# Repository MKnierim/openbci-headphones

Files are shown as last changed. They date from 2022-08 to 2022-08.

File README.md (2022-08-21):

# OpenBCI Headphones
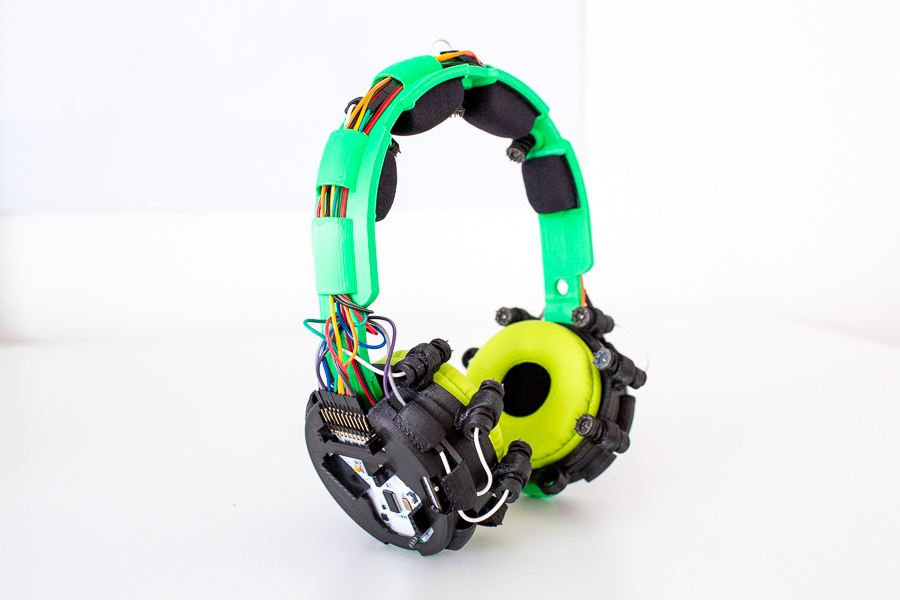
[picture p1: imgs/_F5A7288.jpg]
"The OpenBCI Headphones" The OpenBCI Headphones


If we want our science and technology to grow faster, we need to get more people on it, right?

This repository contains the description and materials for turning the OpenBCI EXG biosignal acquisition system into 
a pair of functional headphones that can also record EEG, EMG, and ECG.

A first validation study is accepted for publication at the <a href="research/Knierim et al. (forthcoming).pdf">43rd International Conference on Information Systems, Copenhagen 2022</a>. You can find the authors' version of this study in the <a href="research/">research</a> folder.

Please take a look at the sections below and the other repository files for assembly details.

If you have any questions, feedback or suggestions, please feel free to send a message to contact@expeeeriments.io

------

# Resources
This project could not have been completed without the wonderful work by other open-source projects. 
Basically, this work is based heavily on these three projects:

1. <a href="https://docs.openbci.com/" target="_blank">OpenBCI</a> (Biosensing Components)
2. <a href="http://www.print.plus/" target="_blank">Print.Plus Headphones</a> (Headphones Design)
3. <a href="https://homebrewheadphones.com/" target="_blank">HomeBrew Headphones</a> (Audio Speakers)

All materials of those (and this project) are available under the Creative Commons Share-alike 4.0 International license.

------

# List of Materials

| Amount | Part   Description                                                  | Instance /   Reference                                                                                               |
|--------|---------------------------------------------------------------------|----------------------------------------------------------------------------------------------------------------------|
| 1      | OpenBCI Cyton Board + Ultracortex Electrodes   (Biosignal Acquisition Kit) | Available from the manufacturer at: https://shop.openbci.com/products/d-i-y-neurotechnologists-starter-kit?variant=13043169493064   |
| 1      | 3D-Printed Headphones Kit (incl. Headband, Speakers, and Electrodes)  | Custom [3D-Print Files](./stl/) available in this repository                                                        |
| 1      | Headband Cushion (kwmobile Sennheiser HD545 replacement)             | Available, e.g. at: https://www.amazon.de/gp/product/B08C57V9H9/ref=ppx_yo_dt_b_asin_title_o00_s00?ie=UTF8&psc=1             |
| 2      | Ear Cushions (70mm diameter)                                         | Available, e.g. at: https://de.aliexpress.com/item/1005002212424250.html?gatewayAdapt=glo2deu&spm=a2g0o.9042311.0.0.dcd44c4deRtu6F             |
| 2      | Audio Drivers (Dayton Audio CE38MB-32 1-1/2"" Mini Speaker)          | Available, e.g. at: https://www.parts-express.com/Dayton-Audio-CE38MB-32-1-1-2-Mini-Speaker-Black-32-Ohm-285-131                               |
| 2      | Audio Jacks (2.5mm)                                                  | Available, e.g. at: https://www.amazon.de/gp/product/B009D5388O/ref=ox_sc_act_title_1?smid=A2X1ST6CC1USDW&psc=1                               |
| 2      | Hookup Wire (4x10cm long)                                            | Available, e.g. at: https://www.adafruit.com/product/288                               |
| 1      | Speaker Cable (Sol Republic Master Tracks HD V8 V10 V12 X3)          | Available, e.g. at: http://shorturl.at/szBKM                               |
| 10     | Jumper Connector Cables Female-Male (10cm, 20cm & 40cm)              | Available, e.g. at: https://www.adafruit.com/product/1953                                                      |
| 1      | Lithium Ion Polymer Battery - 3.7v 500mAh (JST-PH Connector)             | Available, e.g. at: https://www.adafruit.com/product/1578
| 1      | Lithium Ion Polymer Battery 500mm Extension Cable (JST-PH Connector)        | Available, e.g. at: https://www.adafruit.com/product/1131                                          

Lastly, in terms of **tools**, you will definitely need: 

- Soldering iron (to assemble the audio drivers)
- Small screwdriver (to assemble the electrodes)
- Pair of scissors (to cut the headband cushion)

------

# Assembly Instructions
To put the headphones together, you need to first make sure that you have all the required components ready. 
That means sourcing the components and, if you decide so, 3D-printing the headphone parts.
The picture below shows all components and required tools in one place.

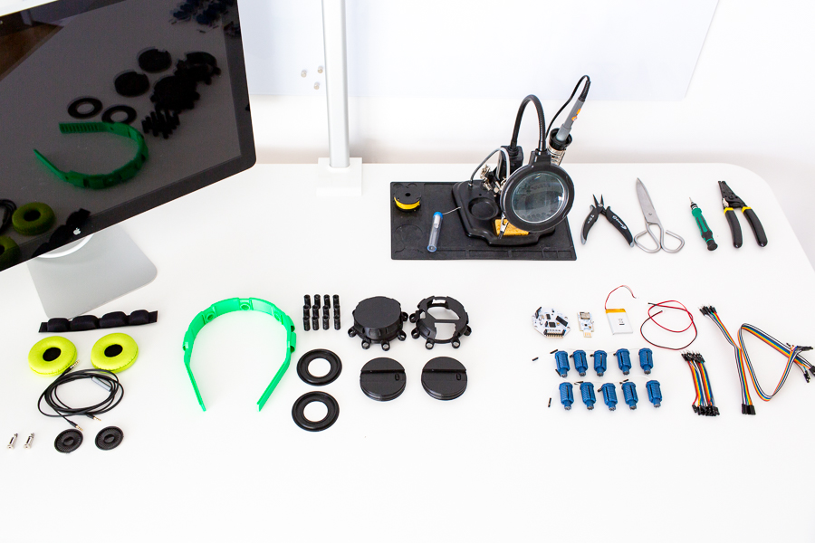
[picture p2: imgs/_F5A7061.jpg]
"All Components Laid Out" All Components Laid Out

 
## 3D-Print the Parts
All of the 3D-printed parts can be manufactured using a regular desktop FDM printer with a 0.4mm brass nozzle and consumer-grade plastics (e.g. PLA).
Importantly, you don't have to set up any particular support structures. These are either not required or already modeled in.
However, some of the parts have particular requirements in terms of stiffness and strength. Therefore, we recommend selecting
appropriate materials for these parts. 

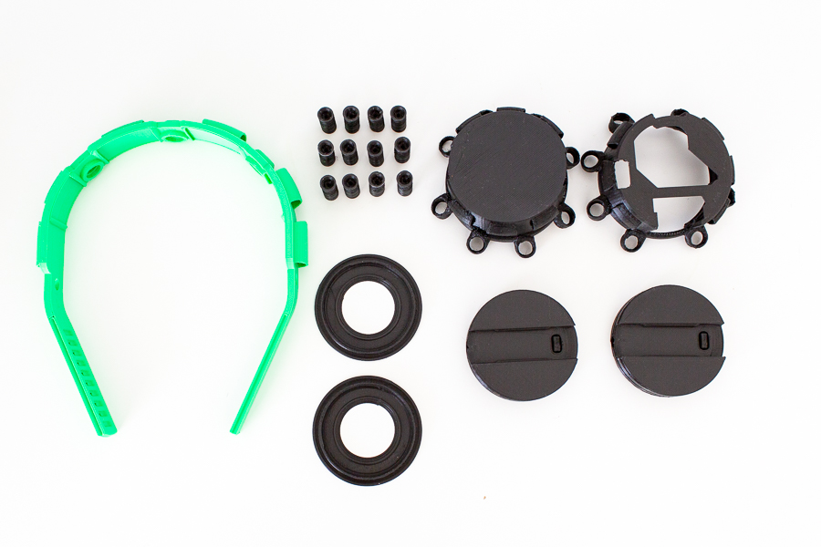
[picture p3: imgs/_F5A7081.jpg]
"All 3D-Printed Parts Laid Out" All 3D-Printed Parts Laid Out
 

### Headband
It is of particular importance for the headband to achieve a high level of flexibility (a low level of stiffness).  
As the headband must bend sufficiently, a more elastic material prevents the headband from breaking during regular use.
Believe us, it happened more times than we'd like to admit during testing... Nevertheless, that helped us figure out suitable materials.
To date, we used the <a href="https://www.extrudr.com/en/products/catalogue/pla-nx2-signalgrun_1980/" target="_blank">PLA NX2 from extrudr</a> 
as it provides the highest material flexibility that we found. The <a href="https://www.ultrafusefff.com/product/ultrafuse-pla-blue-1-75mm-750g/" target="_blank">Ultrafuse PLA from BASF</a>
also works fairly well, as does the <a href="https://fiberlogy.com/en/fiberlogy-filaments/filament-easy-pla/" target="_blank">EASY PLA from fiberlogy</a>. In contrast, the <a href="https://www.extrudr.com/en/products/catalogue/green-tec-pro-schwarz_2284/" target="_blank">GreenTEC Pro from extrudr</a>, 
which we recommend for parts that need to be robust was found to be much too stiff for good use with the headband.

Beyond the right material, it is only important to prevent warping during the print, as already low warping levels can cause the 
electrode holes to become distorted and unusable. Therefore, we recommend printing at lower temperatures and slow speeds to allow for sufficient material cooling. 
A layer height of 0.2mm is sufficient for this part. Also, you might want to try to print with low infill to retain the flexibility (5-10%).

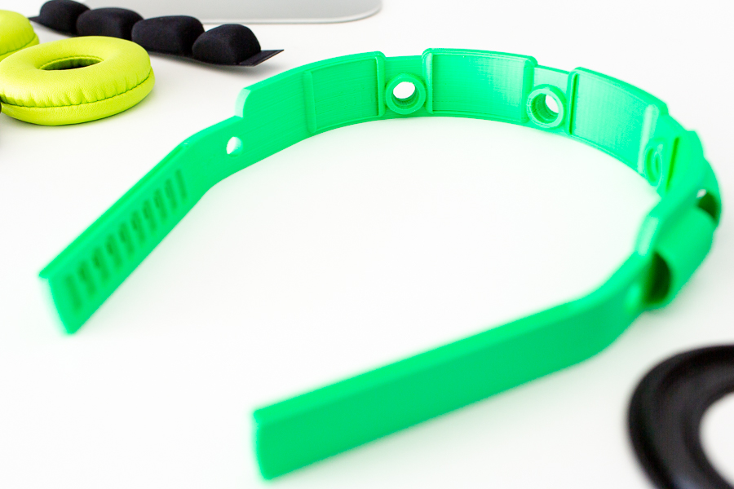
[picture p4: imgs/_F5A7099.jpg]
"The 3D-Printed Headband - PLA NX2" The 3D-Printed Headband - PLA NX2


### Electrodes
As mentioned above, we recommend using a material with high stiffness like the <a href="https://www.extrudr.com/en/products/catalogue/green-tec-pro-schwarz_2284/" target="_blank">GreenTEC Pro from extrudr</a> to print the spring electrodes. 
This material also provides the advantage that it basically does not warp at all. With good retraction settings and 
slow print speeds, you can achieve robust and clean spring electrode prints. 
Also, we printed our electrodes with 0.1mm layer height to make the overhangs print cleaner.

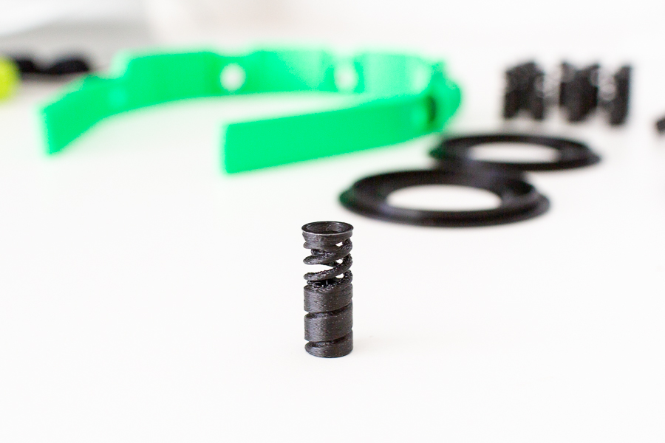
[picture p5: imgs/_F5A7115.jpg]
"The 3D-Printed Spring Electrodes - GreenTEC Pro" The 3D-Printed Spring Electrodes - GreenTEC Pro

 
### Remaining Parts
The remaining parts don't have any particular requirements for printing. You can choose a material that you prefer and 
print them with a regular layer height of 0.2mm at moderate speeds (30-40 mm/s). 
In our screenshots, we used the <a href="https://www.extrudr.com/en/products/catalogue/green-tec-pro-schwarz_2284/" target="_blank">GreenTEC Pro</a> material again for these parts.
 
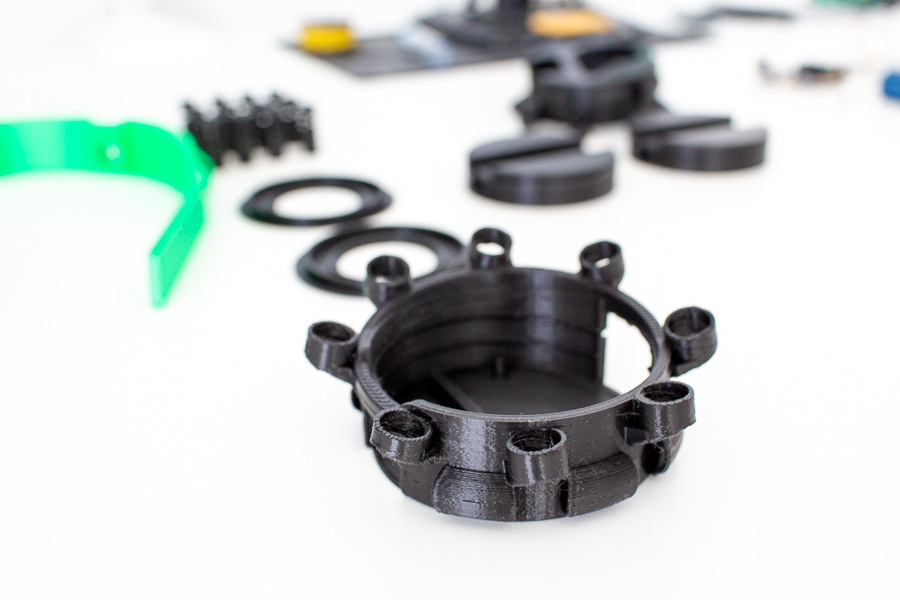
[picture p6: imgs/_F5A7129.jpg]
"The Remaining 3D-Printed Parts - GreenTEC Pro" The Remaining 3D-Printed Parts - GreenTEC Pro


## Electrode Assembly
To finalize the spring electrodes, you need to convert the OpenBCI Ultracortex MK IV electrodes next.
This step is pretty straightforward. 
Use a small screwdriver to screw off the spike electrodes from their original bodies.

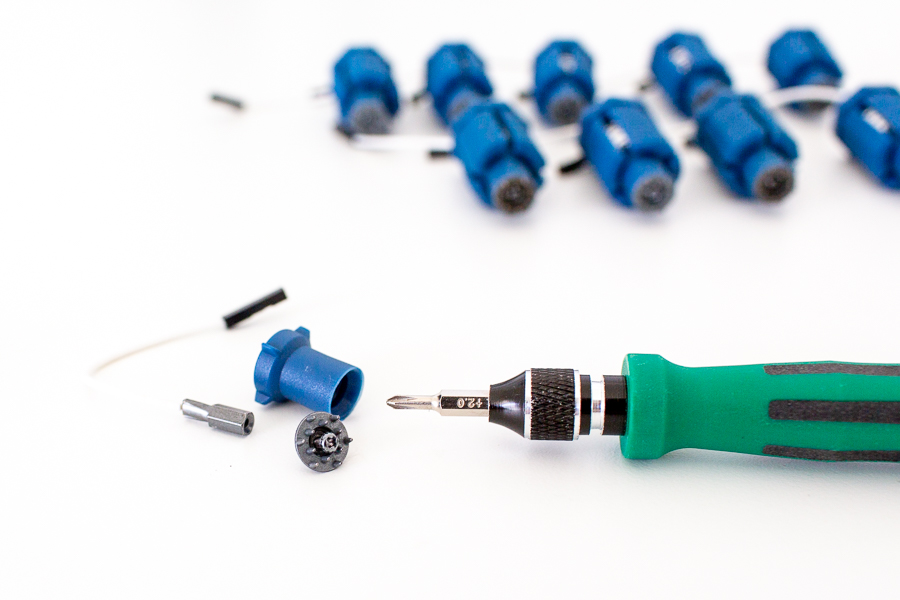
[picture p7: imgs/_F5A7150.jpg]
"Dismantling the OpenBCI Electrodes" Dismantling the OpenBCI Electrodes

 
Afterwards, place first the terminal into the spring electrode. You might have to use your screwdriver to push them in.
Be careful, though, to not damage the cable as it can fairly easily become separated if you apply too much force at the end of the crimp terminal.
Once the terminal is inserted, place the spike electrode on the top, push the electrode together slightly and tighten the screw again. 
Do this a couple of times, and voilà - you have a nice set of 3D-printed headphone electrodes. 

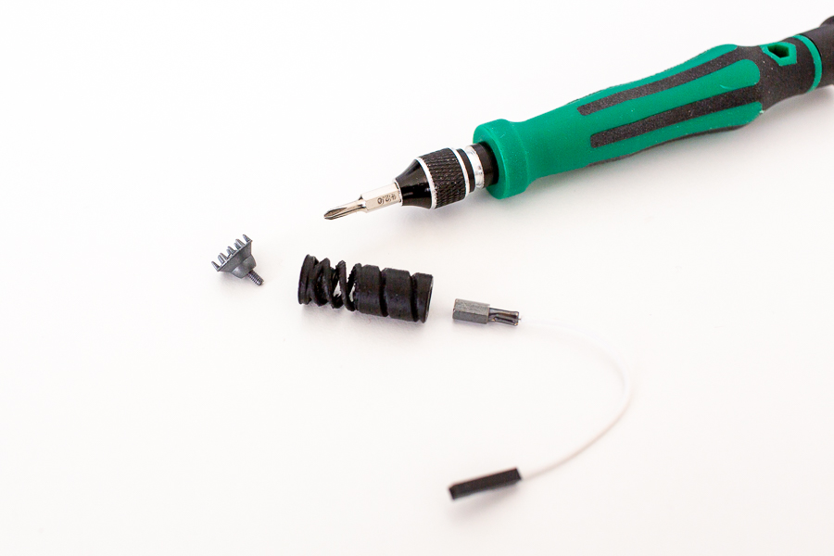
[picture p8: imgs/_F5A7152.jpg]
"Assemble the Spring Electrodes" Assembling the Spring Electrodes


## Cushion Assembly
Next, you can ready the headband and speaker covers by attaching the cushions. 
Having these cushions is super important to achieve decent wearing comfort.
To complete this step, you will require only a pair of scissors.

The headband cushion piece can be cut off at the bridges between the pads.

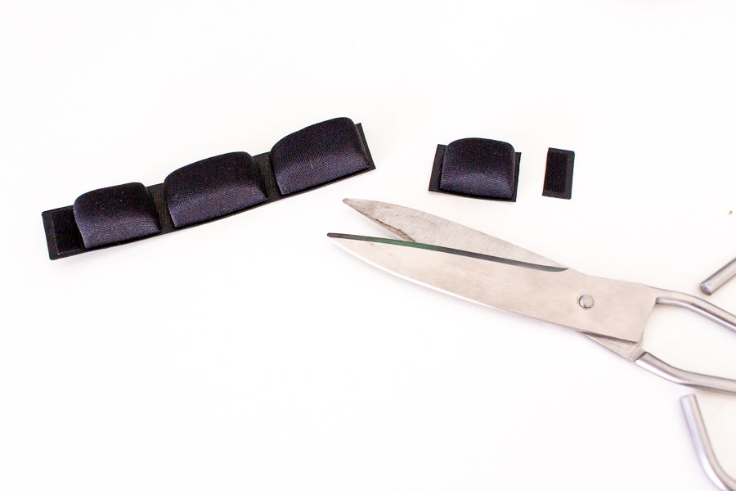
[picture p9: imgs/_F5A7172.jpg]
"Cutting the Headband Pad into Pieces" Cutting the Headband Pad into Pieces
 

Once you have done this, you can start inserting the individual pads into the headband. 
It might take a few tries to cut them to the correct size. 
Leave a slight overhang at each pad to make sure the pad is kept in place by some pressure. 

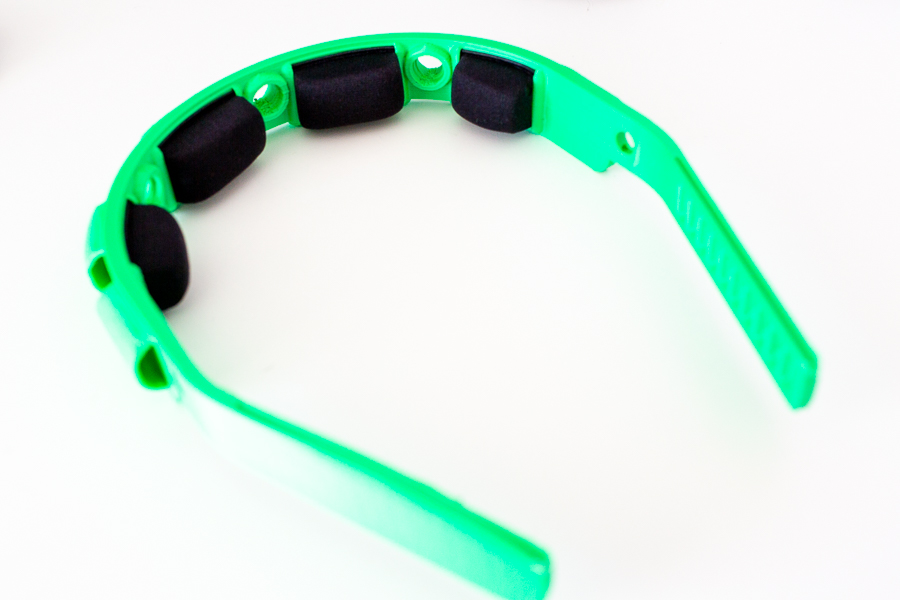
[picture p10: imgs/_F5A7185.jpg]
"Placing the Cushions into the Headband" Placing the Cushions into the Headband


For the speaker cover, stretch the fabric a bit over the cover to attach the cushion.
Piece of cake. It can take some fabric wrestling, though, on the first try.

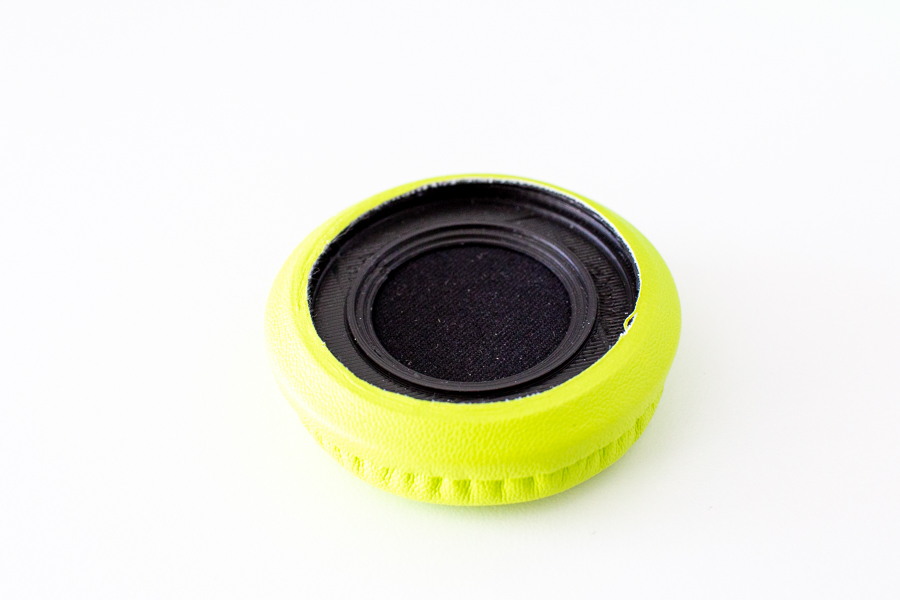
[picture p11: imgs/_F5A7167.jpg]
"Placing the Ear Cushions over the Speaker Cover" Placing the Ear Cushions over the Speaker Cover


## Speaker Assembly
For the assembly of the speaker, we folloed the instructions of the <a href="https://homebrewheadphones.com/build/" target="_blank">HomeBrew Headphones</a> closely. 
You could follow that link and get the same (and extended) instructions. We just include them here again for completeness.

First, you need to solder the hookup wire to the 2.5mm jacks. 
Cut the hookup wire into four approx 2″ or 5cm lengths and strip the insulation from about 1/8″ or 3mm from the ends.
If you are using the recommended jacks, solder the negative (green) wire onto the large tab and the positive (yellow) onto the small round one.

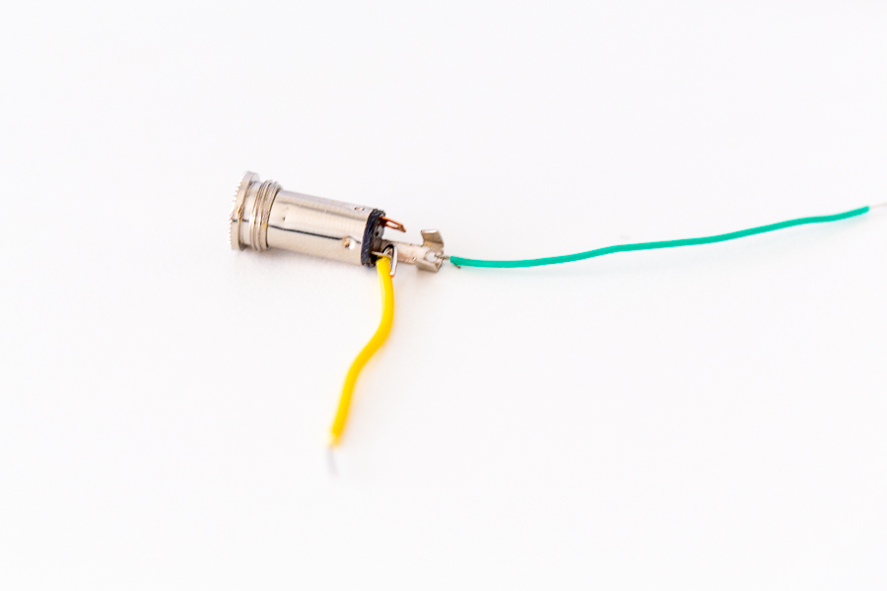
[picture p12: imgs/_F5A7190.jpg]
"Audio Jacks with Soldered Wires" Audio Jacks with Soldered Wires


Next, you can place the audio jacks and drivers into the speaker housing (see picture below).
Be careful not to damage the fragile mylar film in the drivers.
Afterwards, you can solder the hookup wires to the audio drivers. 
The red terminal is positive, and the other is negative. 
You won’t need any solder for this – melt the solder tab on the driver with your soldering iron, then insert the wire into the puddle and remove the iron while still holding the wire until the solder solidifies. 
Be careful not to apply too much heat, as this may damage the driver.

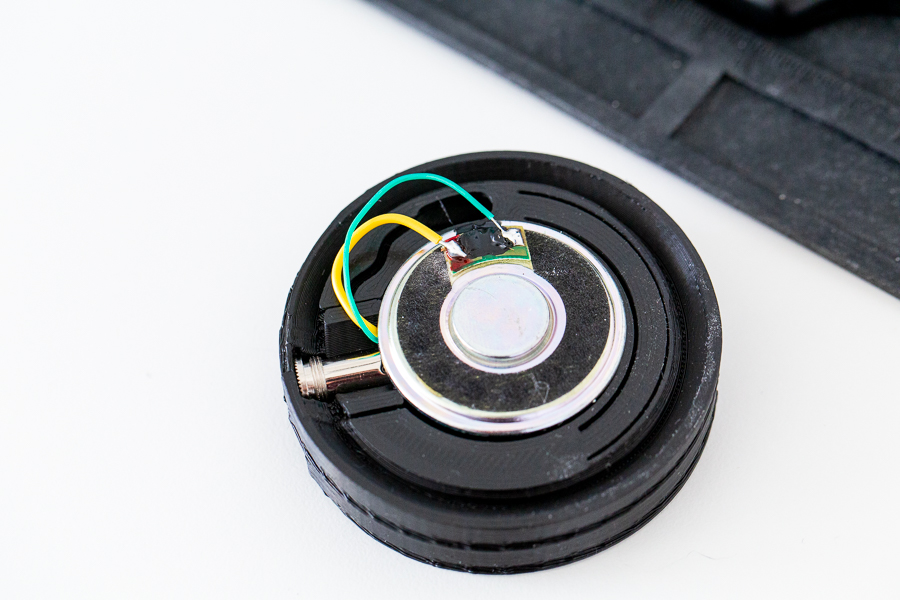
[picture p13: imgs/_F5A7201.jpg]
"Audio Driver Connected to Audio Jack" Audio Driver Connected to Audio Jack


If you would like to tune the sound, please take a look at the <a href="https://homebrewheadphones.com/build/" target="_blank">HomeBrew Headphones build instructions</a> where a thorough documentation is provided for this step.

Finally, to complete the speaker assembly, place the speaker cover with the ear cushions on top and twist to lock them in place. Ta daaaa - you have got some real headphone speakers - assembled all by yourself!

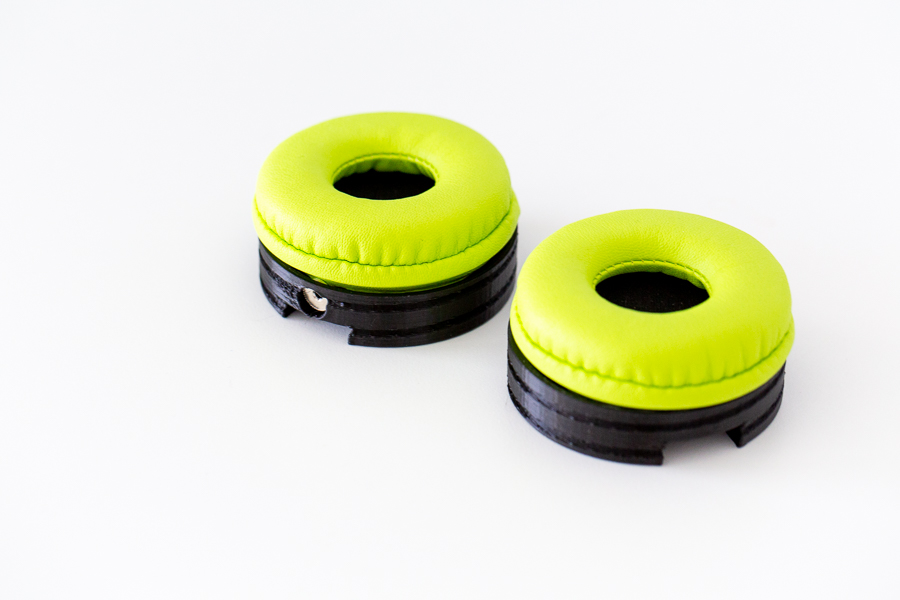
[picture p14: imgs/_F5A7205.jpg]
"Assembled Left and Right Speakers" Assembled Left and Right Speakers


## Electronics Assembly
After all components are ready, you can now finally put the headset together. 
To do this, first, place the battery and Cyton board into the electronics enclosures.
For the Cyton board, attach the battery extension cable already.

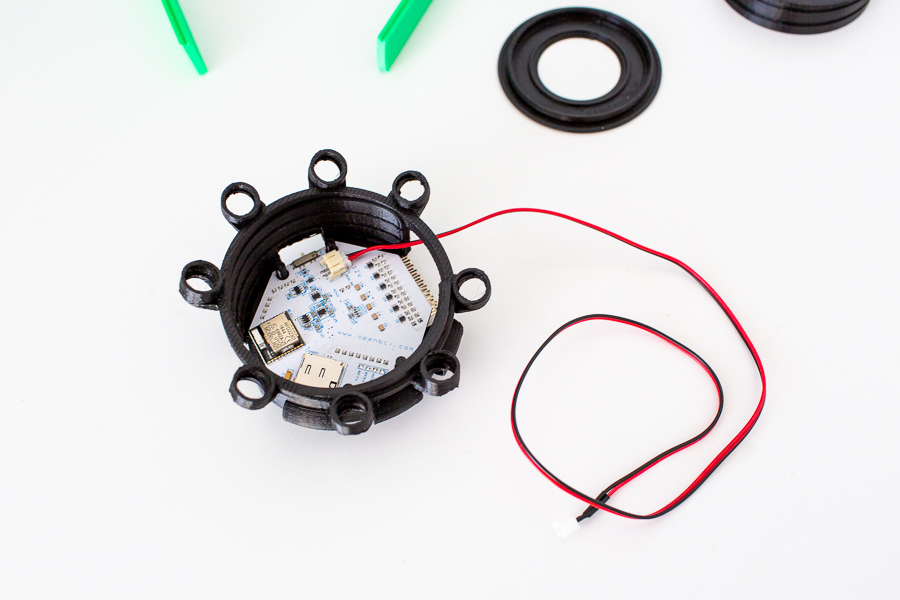
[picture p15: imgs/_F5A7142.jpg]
"Cyton Board in Housing" Cyton Board in Housing

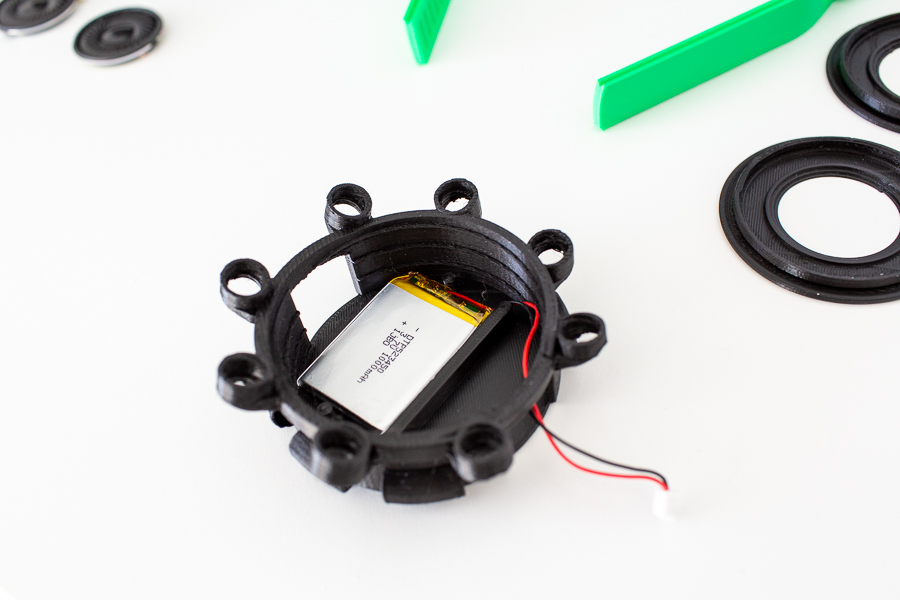
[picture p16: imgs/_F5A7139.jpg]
"LiPo Battery in Housing" LiPo Battery in Housing
 

Now, screw in the assembled speakers. Make sure that the battery cables are sticking out of the enclosure for this.

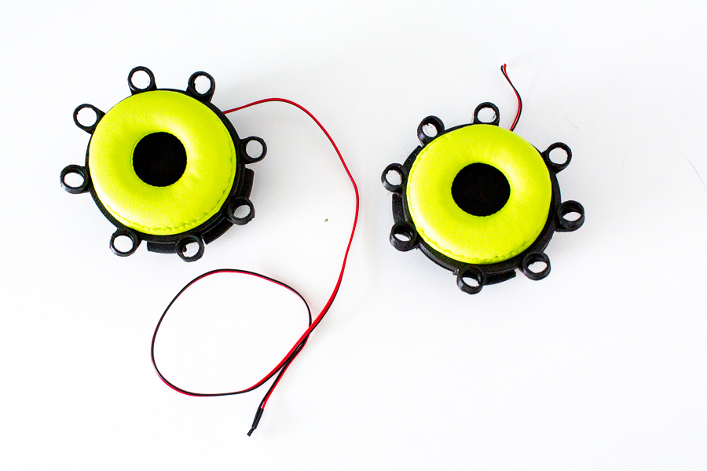
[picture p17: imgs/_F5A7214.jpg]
"Speakers and Electronics Housings Joined" Speakers and Electronics Housings Joined
 

Next, attach the headband to both the left and right speakers. After this, you can route the battery cable from 
the left to the right ear. Test if the Cyton board can be powered on before continuing.
  
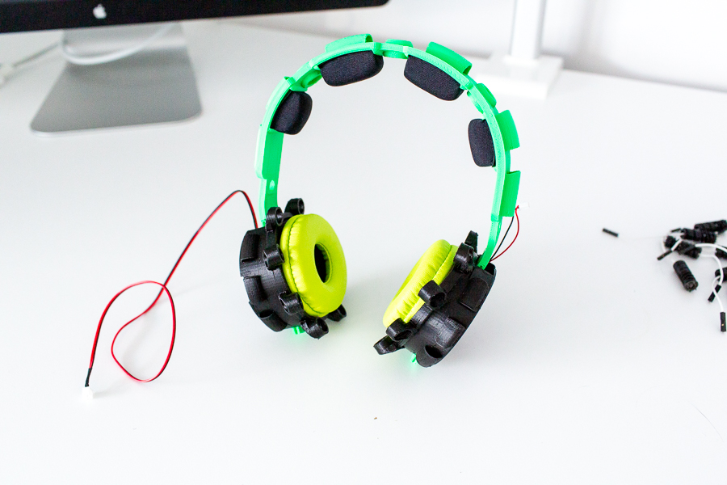
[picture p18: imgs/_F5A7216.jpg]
"Headband and Speakers Combined" Headband and Speakers Combined


At this stage, things are starting to look like headphones, right? Now the only thing left to do is to attach the
electrodes. No electrodes - no electrophysiological sensing. The electrodes screw in the holders easily. Before you start
screwing around, you should take a second though, to consider which electrode positions you would like to use in your recordings.
As the Cyton board can only fit 8 channels (+ reference and ground electrode), your selection for the electrode positions
should be rooted in the phenomenon you are interested in measuring.

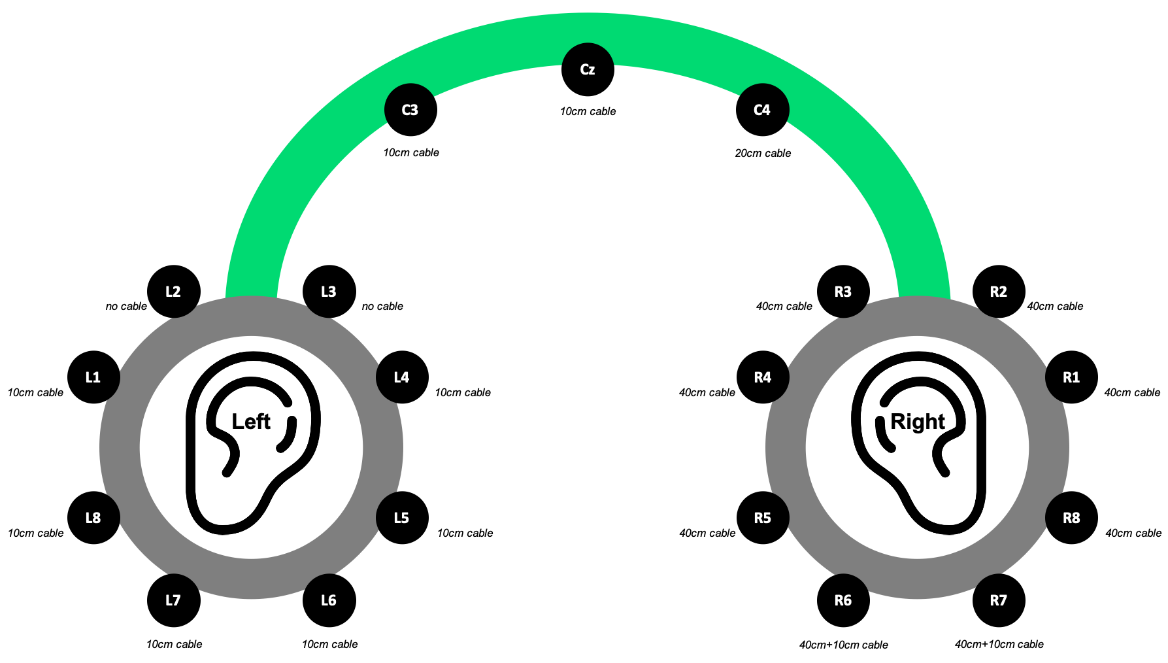
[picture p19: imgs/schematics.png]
"Electrode Position Schematics" Electrode Position Schematics


Once you have decided, screw the electrodes into their holders and attach the jumper wires. 
Route the wires through the cable ducts and onto the Cyton board (in the bottom row!).
We recommend using the same color scheme as in OpenBCI GUI for the different channels (see screenshot below).
This will help immensely later on if you have trouble achieving good contact at a specific electrode position.
For the Cyton board, the reference electrode needs to be attached to the first pin (SRB2 pin), the ground electrode 
needs to be attached to the penultimate pin (BIAS pin). For more details on how to set up the Cyton to record EEG, 
please take a look at the <a href="https://docs.openbci.com/GettingStarted/Boards/CytonGS/" target="_blank">excellent documentation from OpenBCI</a>.  

Well, that is really it. You are set up and ready to go! This is what your resulting headset should look like during this final setup step:

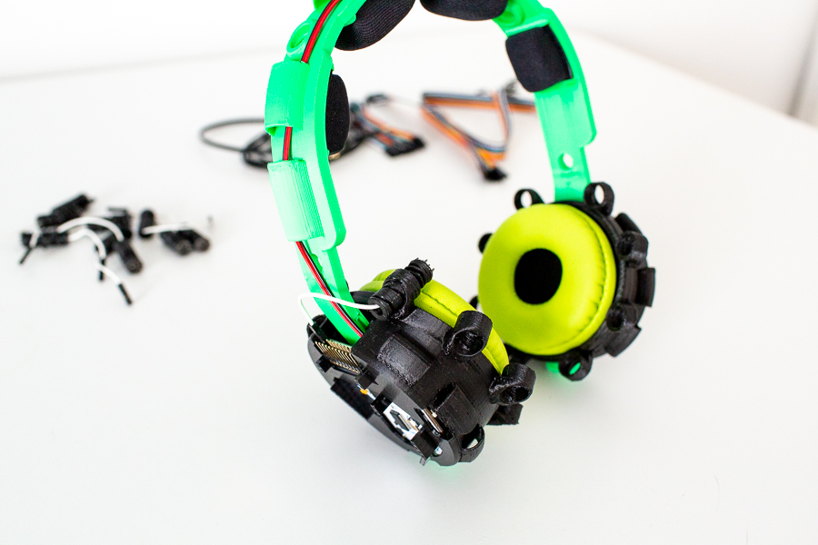
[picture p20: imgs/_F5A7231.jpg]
"First Headband Electrode Attached" First Headband Electrode Attached

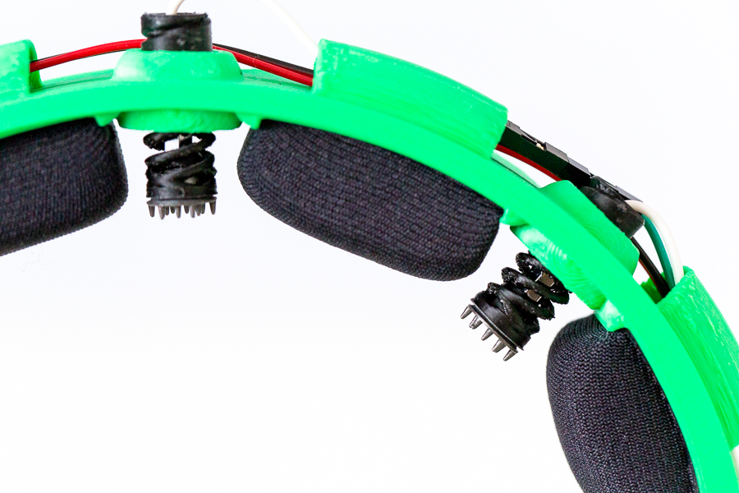
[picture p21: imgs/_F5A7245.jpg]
"Electrodes in Headband Close-Up" Electrodes in Headband Close-Up

"Headband Electrodes Fully Assembled" Headband Electrodes Fully Assembled

## Alternative Assemblies
Even though we have not tried this, we'd like to highlight here, that these EEG headphones can theoretically be 
easily adjusted in terms of channels and component cost. For example, you can double the number of available channels (to 16 + ref & gnd)
by attaching an <a href="https://shop.openbci.com/products/cyton-daisy-biosensing-boards-16-channel" target="_blank">OpenBCI Daisy</a> board to the Cyton board. However, this might require increasing the cable duct size to properly
stow away all the additional wires.  

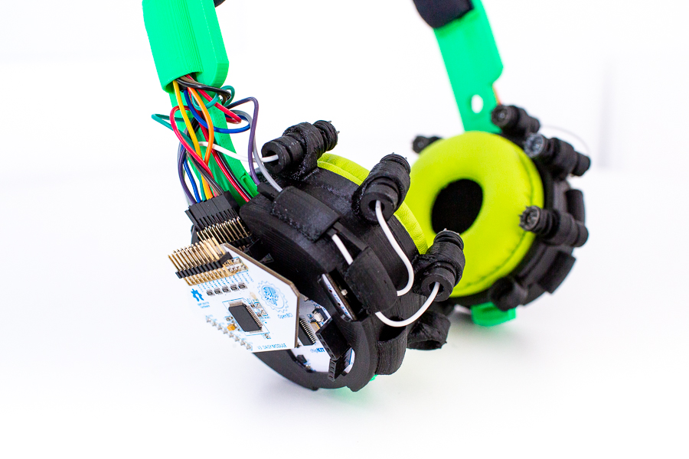
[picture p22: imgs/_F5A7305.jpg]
"Daisy Shield on Headphones" Daisy Shield on Headphones


Similarly, you can reduce the number of channels (and the cost of the electronics components) by using the <a href="https://shop.openbci.com/products/bundle2" target="_blank">OpenBCI Ganglion</a> board instead (4 channels + ref & gnd).
Beware, however, that the OpenBCI Ultracortex are not typically shipped with the Ganglion board. 
Also, the left ear cover might require some adjustment of the surface cut-outs to account for the slightly different stack headers on the Ganglion board.  

------

# Use
To use the headphones for recording electrophysiological data (EEG, EMG, ECG), follow these instructions.

First, if you want to use audio (speaker and microphone), plug the audio cable into the audio jacks 
on the left and right ear and connect the other and to your PC.

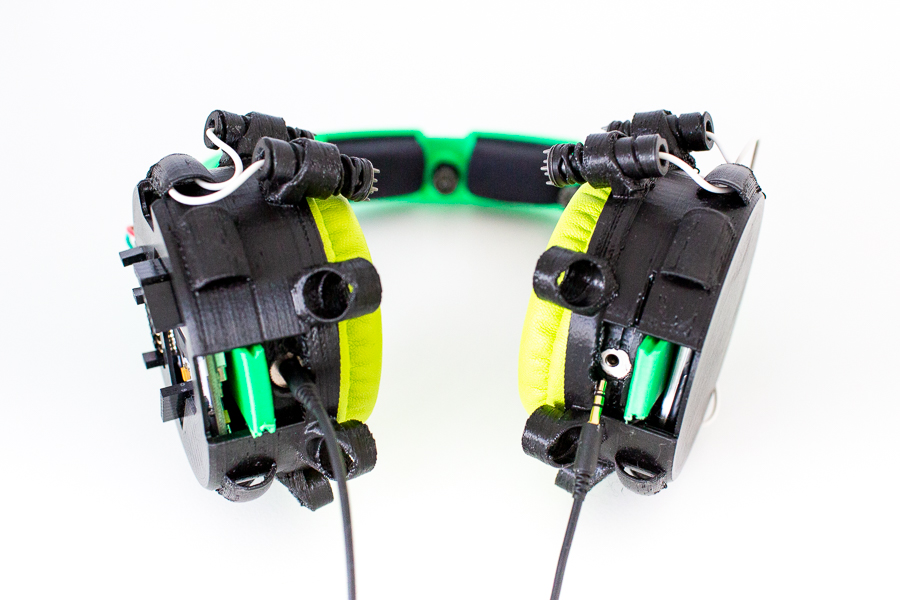
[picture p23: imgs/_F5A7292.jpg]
"Audio Cable Inserted" Audio Cable Inserted


Next, turn on the power on the Cyton board. You can either push the lever up or down 
(the middle position turns the device off). The blue LED will show you that the device is powered on. 
If it doesn't power on, check that your battery is charged (see the instructions below on that).  
 
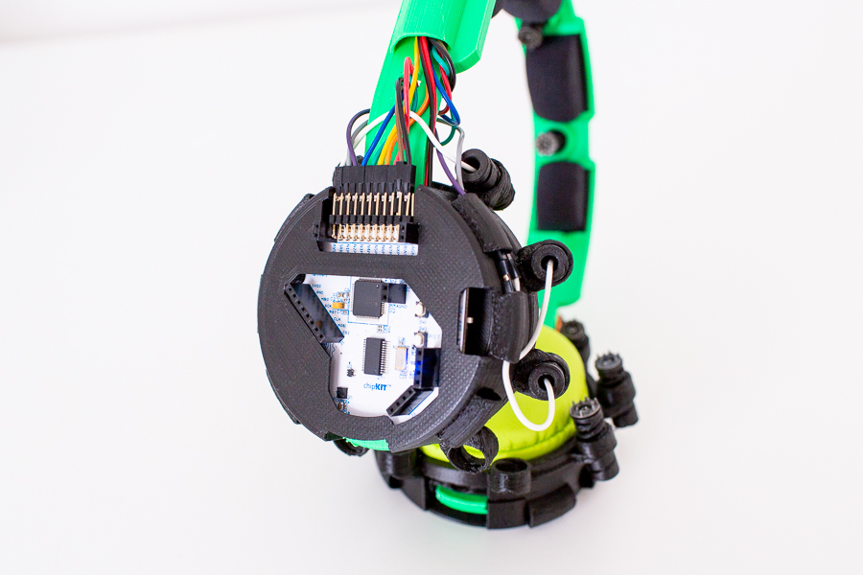
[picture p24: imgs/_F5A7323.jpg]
"Cyton Powered On" Cyton Powered On


Put the headphones on your head now so that they are sitting comfortably. 
Twist the electrodes until they have firm contact with the skin (try to get some hair out of the way if you can). 
You need good skin contact for clean recordings, and that means slight pressure is required. Don't overdo it though. 
It should be sufficient to feel some contact, but it is not necessary to hurt yourself.
Also, please be patient with this initial fitting. The process will be quicker in future sessions.

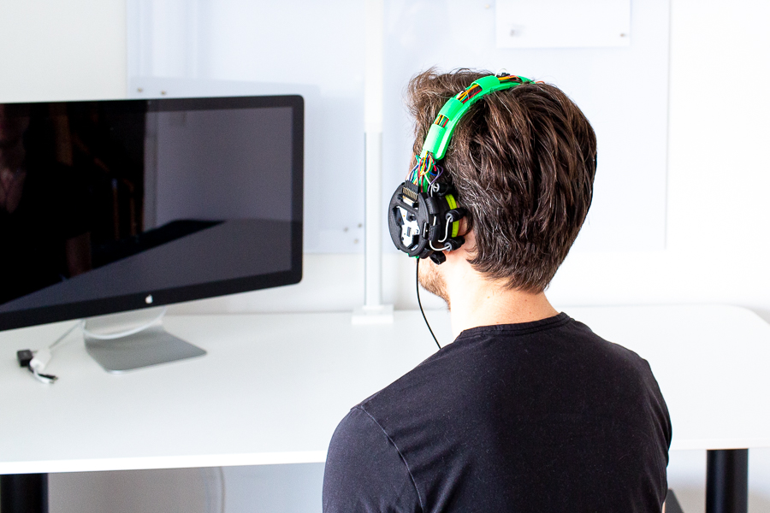
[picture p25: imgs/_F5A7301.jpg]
"Headset on Head" Headset on Head

 
Finally, before starting a recording, it is important to assess good signal quality. Use the OpenBCI GUI software for this.
Plug in the USB Dongle, then start the OpenBCI GUI recording software. 
To connect to the headphones, click: "System Control Panel" > "LIVE (from Cyton)" > 
"Serial (from Dongle" > "AUTO-CONNECT"

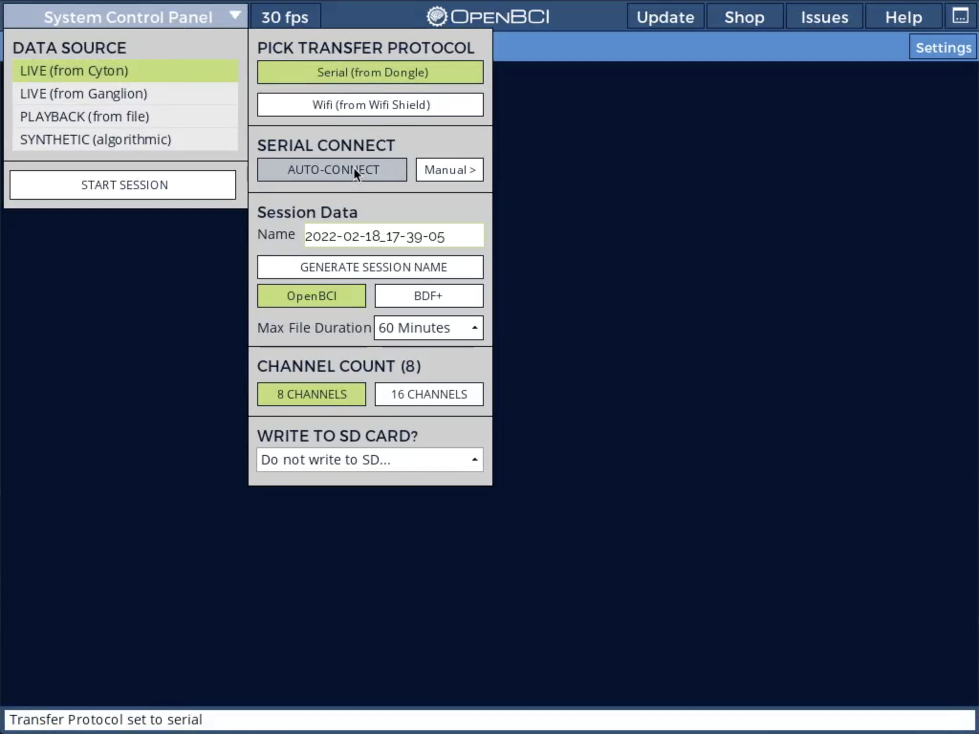
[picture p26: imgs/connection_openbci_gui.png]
"Connecting the Cyton in OpenBCI GUI" Connecting the Cyton in OpenBCI GUI


Keep the default options: 8 channel recording, no SD card recording. Then, finally, click "START SESSION".

Once you see the data coming in, set these filters (in the top view):

- 50Hz Notch (or 60Hz if you are recording in the US - 50Hz is for Europe)
- 5-50Hz Bandpass (this takes care of some low and high-frequency noise)

In the FFT widget panel (on the top right), set these parameters:

- Max Freq: 120Hz
- Max uV: 100uV
- Log/Lin: Linear
- Smooth: 0.9
- Filters?: Filtered

Now, check the amplitudes for each electrode while sitting still for a few seconds. This is very important for the recording!
You'll want to have amplitudes in the range of 5 to 30 uVrms. Also, you'll want to see
similar amplitudes for electrodes in adjacent positions. The spatial resolution of the EEG
is small. So if two electrodes next to each other show very different amplitudes, then something is going wrong. 

Also, in the PSD (top right window) you'll want to see similar curves for all the channels. 
If one channel curve is very different from the others, this typically means that something is wrong with that electrode.
There might be some hair in the way, or the electrode might just have poor contact with the skin.

If a channel seems to be recording badly, try improving the contact with the skin gently. Also, please take a 
few seconds to sit still to assess if your change caused an improvement. Sometimes, high amplitudes can also "just" mean
that the impedances will have to settle a bit. This is normal. Typically, if you set up the headset and wait a few minutes,
you'll get a much cleaner signal impression. If many channels seem to be recording badly, check the reference and ground electrodes
first. Failures in many channels typically mean that these two positions are having a problem.

Eventually, you'll want to see a recording that looks something like this:

Clean Signals in OpenBCI GUI

Ok, you are set up, record away!

# Maintenance
## Charging the Battery
To charge the battery, you only need to detach the battery extension cable from the battery at the right ear. 
Gently pull out the battery cable and sever the extension cable. Be careful not to damage the extension cable by 
pulling too much on the cable itself (i.e. pull on the connector housings instead).

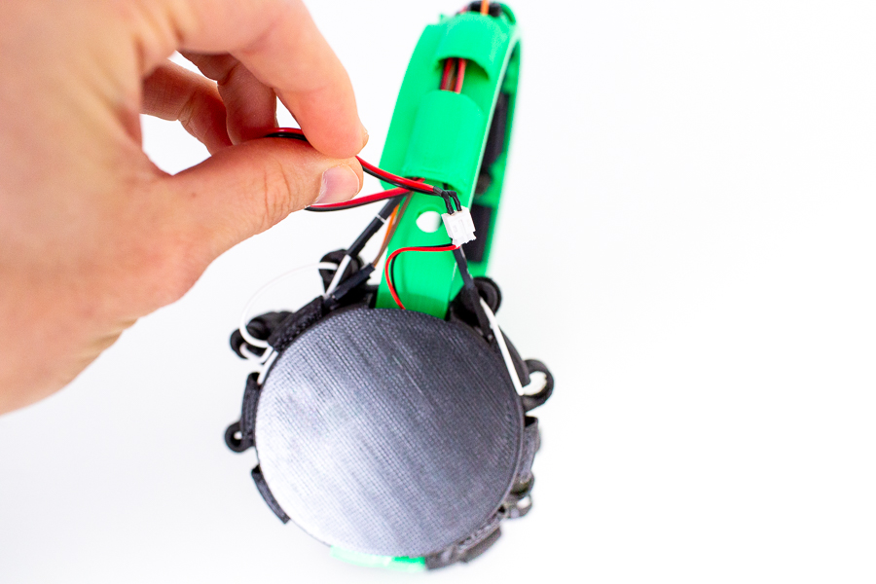
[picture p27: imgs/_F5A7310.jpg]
"Disconnecting the Battery Extension Cable" Disconnecting the Battery Extension Cable


Now, connect the battery to the USB charger. The red light will light up to indicate that the battery is charging. 
Once the red light has turned off, the battery is fully charged again. The 1000mAh LiPo battery that is shown in these
instructions will last for over 12 hours on a single charge.

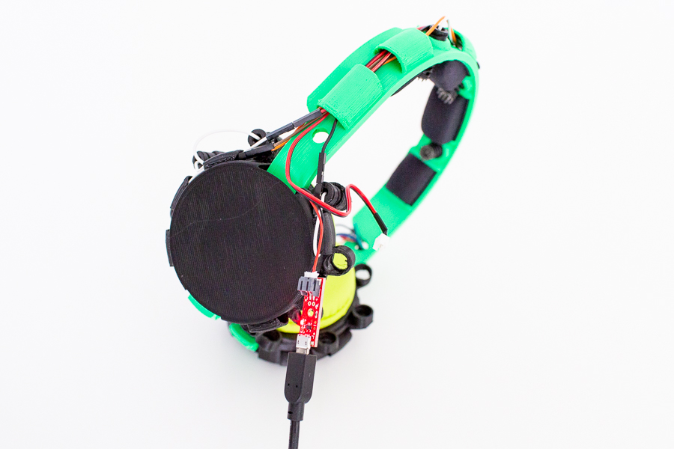
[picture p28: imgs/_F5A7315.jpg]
"Charging the Battery" Charging the Battery
   

## Changing an Electrode
To change an electrode, first, make sure to disconnect the jumper cable from the Cyton board and the electrode itself. 
At this stage, you want to make sure not to damage the electrode cable by twisting it too much while there is tension on it.

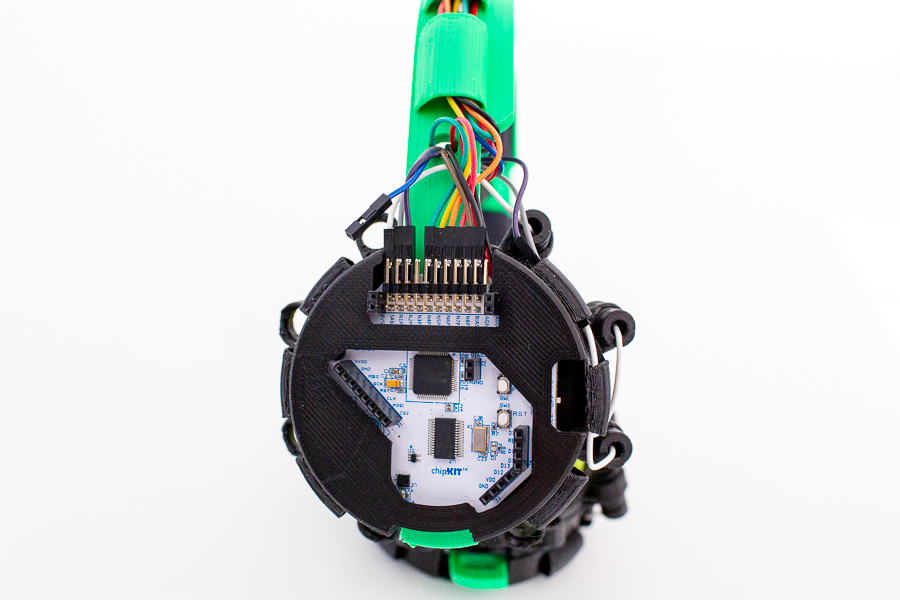
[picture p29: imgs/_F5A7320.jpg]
"Electrode Jumper Wire Disconnected" Electrode Jumper Wire Disconnected


Afterwards, screw the electrode out of its slot, replace it with a new one and connect the jumper wire again. Easy-peasy!

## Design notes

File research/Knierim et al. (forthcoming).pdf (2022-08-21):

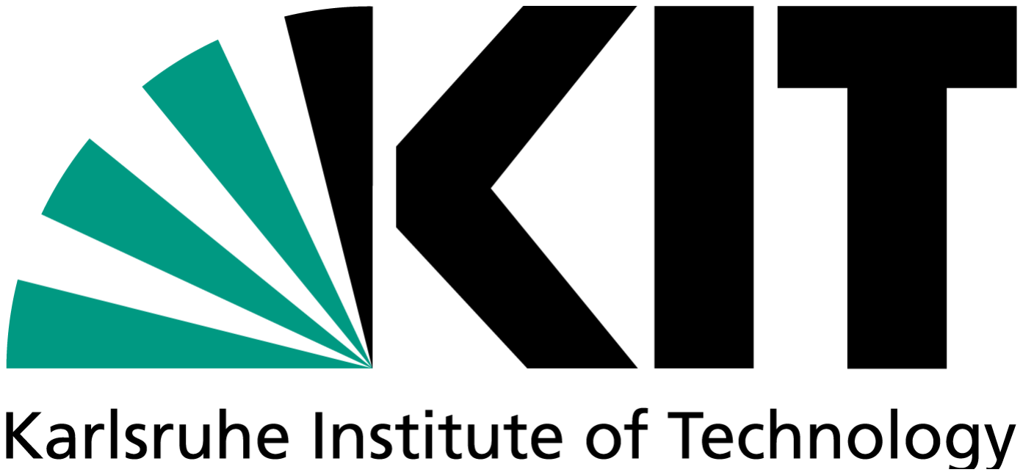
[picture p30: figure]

This is the author’s version of a work that was published in the following source:

Knierim, M. T., Zimny, C., Seitz, J. (forthcoming). Monitoring Cognitive Load with 3D-Printed EEG Headphones. Accepted for Presentation at the 43rd International Conference on Information Systems (ICIS), Copenhagen 2022.

Please note: Copyright is owned by the author and / or the publisher. Commercial use is not allowed.

Institute of Information Systems and Marketing (IISM) Kaiserstr. 93
76131 Karlsruhe - Germany
https://iism.kit.edu

© 2022. This manuscript version is made available under the CC-BY-NC-ND

### 4.0 license http://creativecommons.org/licenses/by-nc-nd/4.0/

Monitoring Cognitive Load With 3D-Printed EEG Headphones

Forty-Third International Conference on Information Systems, Copenhagen 2022 1

# Monitoring Cognitive Load with 3D-Printed EEG Headphones

Completed Research Paper

### Michael Thomas Knierim Karlsruhe Institute of Technology (KIT)

Kaiserstr. 93, 76131 Karlsruhe,

### Germany michael.knierim@kit.edu

### Christian Zimny Karlsruhe Institute of Technology (KIT)

Kaiserstr. 93, 76131 Karlsruhe,

### Germany ubelo@student.kit.edu

### Julia Seitz Karlsruhe Institute of Technology (KIT) Kaiserstr. 93, 76131 Karlsruhe, Germany julia.seitz@kit.edu

### Abstract

Real-world cognitive load monitoring promises to be an essential foundation for positive adaptive information systems that foster knowledge workers’ productivity and well-being. Towards this goal, our research combines established EEG load monitoring principles with low-cost, 3D-printed headphones. This provides a means for continuous, unobtrusive, and real-time cognitive load detection. Results from two experiments document strong relationships of cognitive load reports with EEG frequency bands (Theta and Alpha), both around the ears and on top of the head. While limitations with Theta band power sensitivity are observed, Alpha band modulations are robust across sessions, task repetitions, and three tasks. Furthermore, short setup durations are found, and only minimal influences of hairstyle or glasses on setup times and load relationships. With a discussion of the remaining challenges for more naturalistic studies, this article documents the system’s future potential for load sensing during knowledge work.

Keywords: Cognitive Load, Wearable EEG, Headphones, OpenBCI, Flow Experience, Open-Source, 3D-Printing

### Introduction

Managing mental effort during information system (IS) use in everyday life is an important goal for numerous reasons (Grimes & Valacich, 2015). For instance, related research has most recently demonstrated how cognitive overload can cause detrimental health consequences through the misuse of teleworking-IS during the COVID-19 crisis (Martin et al., 2022). Similarly, earlier works show that general task performance suffers when mental workload increases (Hart & Staveland, 1988) or that knowledge building is impeded by heightened comprehension difficulty (Brünken et al., 2003). Such scenarios can be described as eliciting heightened cognitive load – the mental effort and working memory required to complete a task (Paas et al., 2003). While it is generally not necessary or preferable to eliminate all cognitive load, the ability to monitor disadvantageous load levels has a wide range of practical applications for work, learning, and personal IS use (Grimes & Valacich, 2015; Hu et al., 2017; Lyu et al., 2015). Especially in the expanding domain of knowledge work, the continuous, timely, and unobtrusive monitoring of cognitive load could provide essential benefits for improving productivity, well-being, and growth. For these reasons, scholars are increasingly calling for ubiquitous cognitive load monitoring approaches that could form the foundation of load-regulating adaptive systems and interventions (Grimes & Valacich, 2015; Lyu et al.,

2

2015). Such systems could support knowledge-creating activities by providing recommendations for breaks, goal adjustments, or interruption reductions (Berka et al., 2007; Rissler et al., 2020).
However, it is still a major challenge to assess cognitive load continuously, unobtrusively, robustly, and with high temporal resolution. While several cognitive load measurement methods exist, there is so far no approach that can be used continuously in real-world situations. Self-reports are easily accessible (see, e.g., Hart & Staveland, 1988) but require constant interruption and can not achieve the required continuity and automated support. Behavioral methods, like the load determination by analyzing mouse or eye-movement dynamics, overcome these problems, yet, are limited by a substantial task dependence (Grimes & Valacich, 2015). Neurophysiological measures (e.g., electroencephalography – EEG) have been found to provide robust and cross-task estimators of cognitive load (Berka et al., 2007) and have even already been employed in load-adaptive IT systems (Blankertz et al., 2016; Ewing et al., 2016). Nevertheless, the major downside of this method is the instrumentation itself – EEG measurements typically rely on gelled electrode caps and long and cumbersome setup procedures with hair-washing and skin preparation (Bleichner & Debener, 2017; Riedl et al., 2020)¹. Even some of the more portable systems still often come with alienating aesthetic form factors, which make them impractical for real-world settings. Thus, to enable real-world load monitoring, dry-electrode EEG systems are needed that are set up quickly and blend in seamlessly with existing wearable technologies.
For this purpose, we have transformed the OpenBCI open-source, dry-electrode EEG recording system from a standard, helmet-shaped headgear into a more naturally occurring form factor – a pair of 3D-printed headphones. This design allows using established hardware & sensing principles in a low-cost and reproducible wearable device with a commonly accepted form factor. By keeping the open-source nature of all components and by developing a configurable system, we provide a toolkit for scholars with various backgrounds for the study of cognitive load, especially for knowledge work. With this article, we aim to first answer the following research question: Can cognitive load changes be identified by dry-electrode EEG measurements with sensor locations in the headband and ear regions of typical headphones?
To answer this question, we conduct two controlled laboratory experiments that assess the systems’ general monitoring aptitude across sessions, individuals, and tasks. The results show strong relationships between self-reports of cognitive load and EEG frequency bands, specifically Theta band activity on the top of the head and Alpha band activity both around the ears and on top of the head. While the Theta band relationship shows limitations in terms of reliability and sensitivity, the majority of the observations are highly in line with established EEG findings and document the system’s aptitude for load detection. Importantly, towards applying the system in real-world situations, we refrained from any skin or hair preparation of the participants and collected data from people with various hairstyles, genders and glasses. With short setup durations throughout (less than five minutes on average) and only minimal impact on setup times and main effects, our findings provide a solid foundation for extended work.
Thereby, we contribute to the IS discipline by enabling further research on load monitoring in knowledge work scenarios through the provision of hardware, methodology, and measurement validation. All the materials for replicating the described system (list of components and assembly instructions) are made available with the article. While there are limitations to the real-world use of the EEG features as load indices that we cannot fully assess yet (e.g., the influence of movement on electrode contact and signal artefacts or the influence of time and visual stimulation on frequency band powers), we discuss how future work could address these factors. Finally, we highlight an interesting connected use case in the knowledge work context, that is the possibility to observe flow experience occurrence through cognitive load monitoring, which has been discussed as a desirable vehicle for increased productivity and well-being in knowledge work (Knierim et al., 2019; Rissler et al., 2020). Therefore, the theoretical and empirical integration between cognitive load and flow is discussed at the end of the article as a final contribution, together with a proposed study design to assess the system’s applicability in a more naturalistic setting.

1 The cumbersome experience with gelled EEG systems has even caused public criticism from study participants. The following blog post describes a participant’s ordeal of finding a cleansing agent to remove EEG gel: http://belovedmonsterandme.blogspot.com/2009/01/glue.html - last accessed 17.08.2022.

3

### Theoretical and Conceptual Background

In general, it can be said that cognitive processing consists of two main components, a rather bounded working memory and a much larger long-term memory (Paas et al. 2003). To process an activity, some level of working memory needs to be devoted to the task at hand. This process is referred to as the exerted level of cognitive load (Grimes & Valacich, 2015; Paas et al. 2003). Cognitive load can thereby be categorized into three types: (1) intrinsic load that is related to a specific topic, (2) extraneous load that is related to how tasks are presented, and (3) germane load related to the work needed to store knowledge permanently (Paas et al. 2003). While this conceptual differentiation is useful for assessing load sources, the three facets are not easily differentiated by measurement methods like EEG. Therefore, we continue this article by considering cognitive load as a holistic construct that encompasses the sum of these three load dimensions. A substantial amount of research on cognitive load has investigated the detrimental effects of high load on knowledge building in IT-mediated learning scenarios (Brünken et al., 2003; Paas et al., 2003). Beyond this context, an increasing body of work is emerging in the IS discipline and neighboring fields that documents the critical consequences of (prolonged or extensive) cognitive load in the area of knowledge work. For one, several studies are documenting the adverse impact of high load on task performance, caused, for example, by reduced decision speed and accuracy (Grimes & Valacich, 2015) or by extended information search and evaluation processes (Hu et al., 2017). At the same time, these effects are accompanied by reduced IT-system satisfaction (Hu et al., 2017; Lyu et al., 2015) and can even lead to stress and lowered physical and mental well-being (Galy et al., 2012; Lyu et al., 2015). With the predicted shift of work sectors into the knowledge domain due to the extended AI-computerization of various tasks (Frey & Osborne, 2017), we argue that it will become increasingly important to regularly monitor cognitive load in knowledge work. Several methods can be used to assess cognitive load, including subjective measures (i.e., self-reports), behavioral measures (e.g., learning outcomes), and objective measures like mouse movements, eye-tracking or brain activity (Brünken et al., 2003; Chikhi et al., 2022; Lyu et al., 2015). While each of these approaches provides some insight into the level of experienced cognitive load, they also have shortcomings that researchers and practitioners alike must be aware of – especially when considering which degree of ubiquity and continuity the methods provide for load monitoring. Survey methods suffer from response bias and task interruption, which may lead to confusion, reduction of performance, and dissatisfaction (Grimes & Valacich, 2015). Behavioral methods, like the observation of mouse or eye-movement dynamics are limited by a substantial task dependence (Grimes & Valacich, 2015). For example, in the knowledge work domain, writing code or a scientific article can require minimal mouse activity, and generates specific eye-movements, that are likely very different from, for example, an online-shopping scenario. Neurophysiological measures such as heart rate, pupil dilation, and fMRI can interfere with the natural use of the system, thus inhibiting the user from engaging in their primary task (Grimes & Valacich, 2015). Ubiquitous, real-world load monitoring still needs to overcome the hurdles of high-quality user experiences (comfort, intrusiveness, aesthetics) and high measurement quality (noise and reliability). A promising development in this regard is the recent research on “transparent” EEG (Bleichner & Debener, 2017). Transparent EEG methods focus on collecting neural signal data through hardware systems that are placed on the head at inconspicuous positions, at the moment primarily in ear-adjacent locations (Bleichner & Debener, 2017). In-ear EEG or around-the-ear EEG electrode arrays are found to be usable for high-quality EEG recordings with much higher convenience than standard EEG cap recordings, for example, in situations like speaker attention detection (Bleichner & Debener, 2017) or affect monitoring (Athavipach et al., 2019). Two articles using around-the-ear cEEGrid electrodes also already demonstrate the possible use of ear EEG for workload monitoring in driving simulators (Wascher et al., 2019) and cognitive tasks (Knierim et al., 2021). These works leverage the established principles of EEG load monitoring. The human EEG has been shown to provide reliable estimators of cognitive load through characteristic modulations in the power of EEG frequency bands (Müller-Putz et al., 2015). The most prominent frequency bands with power changes related to cognitive load are Theta and Alpha. Such frequency band activity is derived by decomposing the EEG signal into oscillatory, wave-like patterns (see Figure 1). In general, Theta waves are characterized by low-frequency activity (4–7 Hz) often associated with various sleep phases, mediation, fatigue, and cognitive load patterns (Müller-Putz et al., 2015). Alpha waves, on the other hand, are characterized by medium-frequency activity (8–12 Hz) and generally indicate states of relaxation and readiness (Berger, 1929).

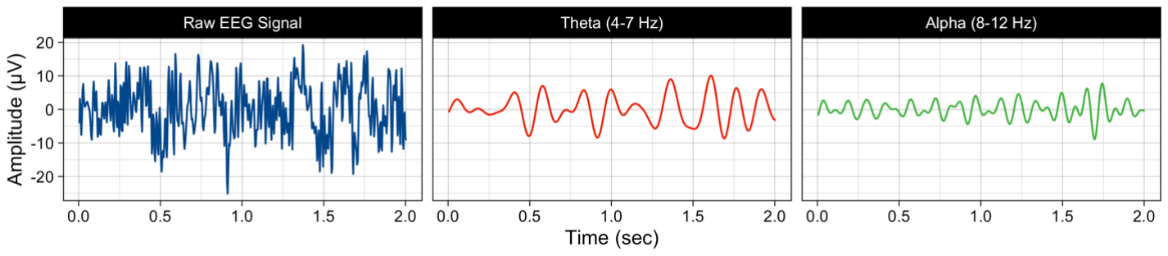
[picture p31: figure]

4

Figure 1. Excerpts of EEG signals with extracted frequency oscillations. The data are from electrode L3 of one study participant during an eyes-closed resting phase. An increase of this wave type is common and prominent during resting periods with closed eyes. The effect is even so prominent, that it can be seen in the raw EEG signal without signal processing – which is why it was observable in the initial development of the EEG method by Hans Berger in 1929. Thereby, the difference of Alpha power (particularly in posterior brain regions) between eyes-open and eyes-closed rest has been called the Berger effect. Based on this finding, scholars have also argued that Alpha waves represent cognitive inactivity, also referred to as cortical “idling” (Müller-Putz et al., 2015). In relation to cognitive load, Theta power has been shown to be positively correlated with load, most notably in frontal regions, whereas Alpha power is typically found to be negatively correlated with load, particularly in parietal regions (Chikhi et al., 2022). As this pattern has been found to be quite robust, it has been affirmed and used repeatedly in IS literature (for a discussion see Müller-Putz et al., 2015). Scholars have also developed dedicated load indices as a combination of lower and higher frequency powers (e.g., Theta/Alpha frequency band power) that can be used to determine load levels across tasks and situations (Berka et al., 2007). In terms of sensitivity, scholars have even reported being able to predict the exact level in a Tetris game using advanced signal processing methods that isolate the modulation of EEG frequencies related to the cognitive load during that level (Blankertz et al., 2016).
In contrast, the previously mentioned ear-EEG studies (Knierim et al., 2021; Wascher et al., 2019) report limitations in differentiating various cognitive load levels, possibly related to the small amplitudes (resulting from smaller electrode distances). Also, using these cEEGrid electrodes still requires the “typical” steps of recording setups, to achieve high signal qualities (skin preparation, gelled electrodes), and a headband mounting solution that is minimal, but still atypical in real-world situations. For these reasons, we have developed an open-source, 3D printed EEG headphone system that features both greater electrode distances (around the ear and with electrodes on the top of the head – positions that are closer to sites typically used for EEG-based load detection – see, e.g., Ewing et al., 2016; Kartali et al., 2019) and dry electrodes which greatly facilitates recording setups. The following chapters describe the key features of this recording system and the studies we conducted to investigate its usefulness for cognitive load monitoring.

### Method & Materials

To develop the dry-electrode EEG headphone system, an available open-source EEG kit and an available open-source headphone project were adapted and joined. This means, that the core of the measurement system is built on established technology, the amplifier and electrodes of the OpenBCI Cyton biosignal acquisition platform. The OpenBCI Cyton amplifier allows 8-channel EEG recordings with a sampling rate of up to 250 Hz, 24 bit resolution, low input-referred noise and low power consumption (Rashid et al., 2018). With a 1000mAh LiPo battery and a 16GB SD card continuous recordings of over 10 hours can be achieved (Knierim et al., 2021). Normally, this amplification system is used with a full head harness, the Ultracortex MK IV (see Figure 2) that features the possibility to use electrode positions of the standard 10-20 reference system (Oostenveld & Praamstra, 2001).
The headphone system, in contrast, allows EEG recordings on three typical electrode positions on the top of the head (C3, Cz, C4), and around the ear, featuring about the same electrode positions that are recorded with the around-the-ear cEEGrid electrodes (Debener et al., 2015) – that we consider as an established reference system for around-the-ear EEG electrode positions. An overview of the available electrode positions in the EEG headphones is shown in Figure 3. Thus, the system’s measurement process is also rooted in established methodology. As the Cyton amplifier allows recording from 8 electrodes (plus

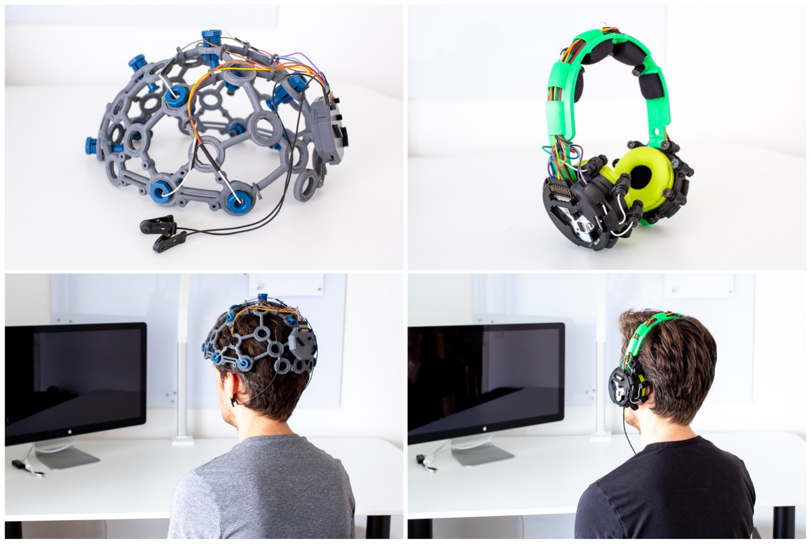
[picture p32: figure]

5

reference and ground electrodes), a choice needs to be made for the desired electrode positions in a particular study. In the two following studies, we used position L4 for the reference electrode and position R2 for the ground electrode. This configuration was chosen to allow re-referencing after the recording to a symmetrical linked mastoid reference (L5+R5), which is repeatedly done in cEEGrid studies (Debener et al., 2015; Wascher et al., 2019). As frontal and posterior electrode locations have been found to play an important role for cognitive load monitoring (Chikhi et al., 2022) we used the top electrodes (C3, Cz, C4) and two electrodes at each ear (L3, L5, R3, R4, R5) in the following studies.

Figure 2. The EEG headphones system (on the right) in comparison to the standard OpenBCI EEG headgear (Ultracortex MK IV) on the left. A similar, but not identical electrode layout configuration is shown. By building on the knowledge from the “Print.Plus” open-source headphones project, we also leveraged established aesthetic and comfort factors for the headphones design. In addition, the headphones can even be fitted with audio drivers to feature a fully functional headphones system with speakers and a microphone – which can both be used during an EEG recording. All of these components can be freely purchased and assembled at low cost. The latter is especially so because the majority of the components can be generated by regular fused-deposition modeling (FDM) desktop 3D-printers (or through 3D-printing services). The materials for fully replicating the described system (list of components and assembly instructions) are provided here: https://github.com/MKnierim/openbci-headphones.
This headphone EEG solution is not the first of its kind (see Kartali et al., 2019 for a study with a commercial analog with saline water electrodes), yet features a few distinct attributes essential for ubiquitous mental state monitoring research: (1) configurability (selectable electrode positions and open-source modifiability of all hardware and software components), (2) dry electrodes (allowing fast setup), and (3) low cost (facilitating research even with smaller budgets). At the same time, it should be acknowledged, that these advantages also come with their own limitations. Dry electrodes are known to provide poorer signal-to-noise ratios (SNR) than gelled (or saline) electrodes and a higher proneness to electrical and mechanical artefacts (Müller-Putz et al., 2015; Riedl et al., 2020). These limitations should be taken into consideration for various research designs. We propose here though, that the reliance on fast study setups and gel-free

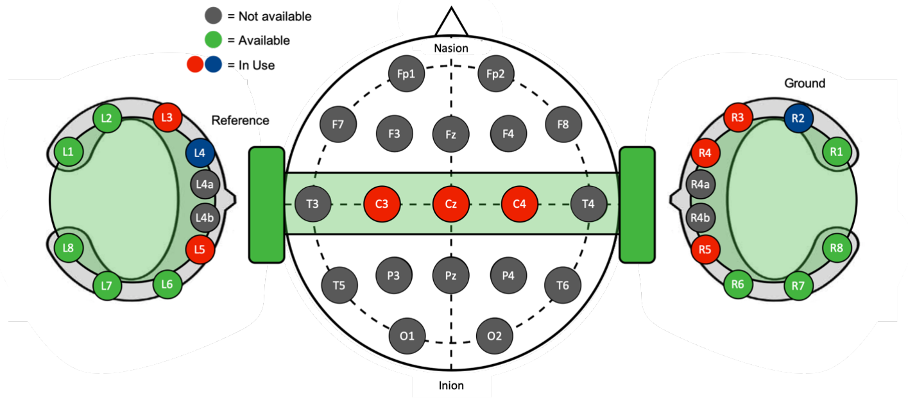
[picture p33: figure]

6

electrodes is likely a key factor in achieving real-world user studies in the long-term. Thus, we argue that our presented system provides a significant bridge into the development of related studies and measurement systems.

Figure 3. Electrode positions in the EEG headphones system. The configuration for the two studies described below is shown with red and blue electrodes. The layout combines the standard 10-20 electrode positioning system for cap EEG (Oostenveld & Praamstra, 2001) and the layout of around-the-ear cEEGrid electrode arrays as main ear electrode positioning reference (Debener et al., 2015). To assess the principle measurement capabilities of the system (without going into detailed signal quality aspects – as these have been generally documented for the OpenBCI Cyton amplifier before – see, e.g., Rashid et al., 2018) and to explore the system’s suitability for monitoring changes in cognitive load, two laboratory studies were conducted. The details and results of these studies are described in the next two chapters in detail. As, however, the processing of the EEG signals was identical in both studies, we outline these steps here.
The signal processing and feature extraction steps were primarily aligned with the related work on cognitive load observation with around-the-ear cEEGrid electrodes (Knierim et al., 2021; Wascher et al., 2019). This means, that for each 90-seconds data segment (each task round of the experiment), the signals were mean-centered and filtered using a 2-30 Hz finite impulse response (FIR) bandpass filter to remove signal drifts and high-frequency noise. Afterwards, data were epoched (2-second sliding windows with 1-second overlap) and noisy epochs (e.g., due to movement artefacts) were removed as determined by the Riemannian potato similarity criterion using a 2 SD threshold (Barthélemy et al., 2019). Next, the recordings were re-referenced to mean averaged linked mastoids (channels L5+R5). Then, the power spectral density (PSD) was estimated for each epoch using the multitaper method which is suggested when more noisy data can be expected (Babadi & Brown, 2014). All band power estimates were relativized (division of each frequency by the sum of all frequency powers), as this has been found to provide more reliable differentiation for workload monitoring (Wascher et al., 2019). To extract the two frequency bands of interest (Theta and Alpha), the individual Alpha frequency (IAF) was determined visually and confirmed with the “transfreq” clustering method (Vallarino et al., 2021) which detects the transition frequency between the Theta and Alpha band. This step was used to obtain higher spectral precision, as the IAF is known to fluctuate substantially between individuals (Müller-Putz et al., 2015). As the Theta and Alpha bands border each other, a frequency bin of 2 Hz between peak Alpha and peak Theta was kept, reducing spillover effects. Each band was determined as ±1.5 Hz from its determined center. The average Alpha range (based on the average Alpha peak of 10Hz) was 8.5 to 11.5 Hz, and the average Theta range 3.5 to 6.5 Hz.

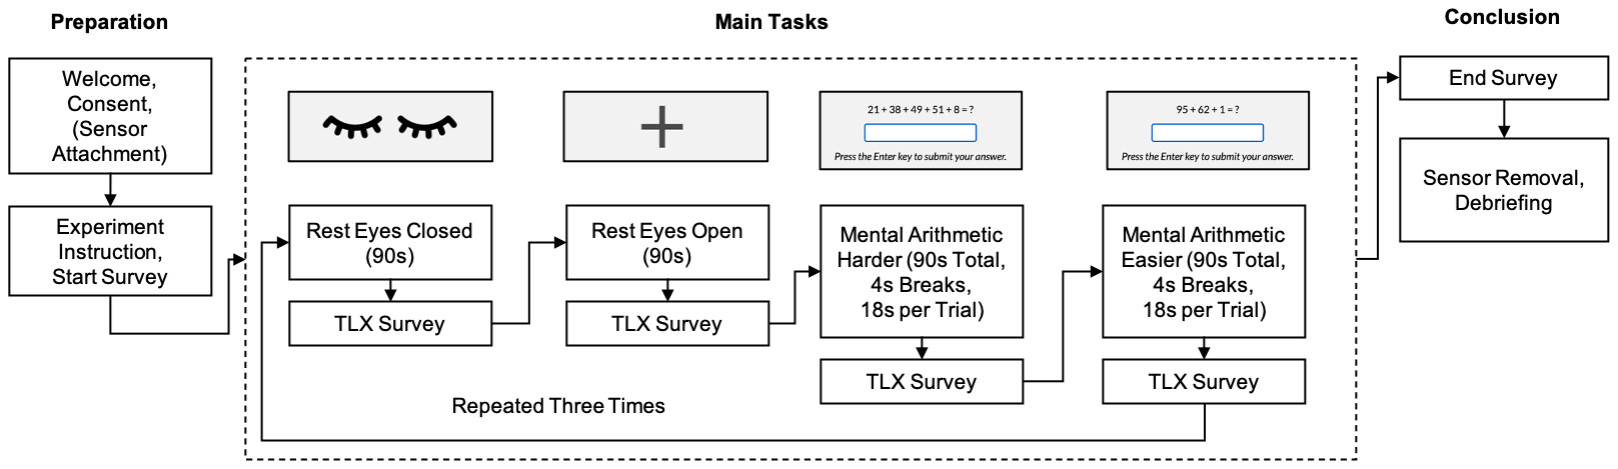
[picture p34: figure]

7

### Study 1

Procedure

To initially assess the potential of the headphones EEG system for neural data collection, a short, controlled experiment was conducted to observe if two main effects can be detected: (1) the Alpha frequency band power increase when eyes are closed (the so-called Berger effect – see, e.g., Debener et al., 2015), and (2) the modulation of Theta and Alpha frequency band powers due to variations in cognitive load. Therefore, the experiment consisted of two task groups: (1) resting phases of eyes-closed and eyes-open rest (with a fixation cross) to study the occurrence of the Berger effect, and (2) a mental arithmetic task in an easier (adding up 3 summands), and a harder condition (adding up 5 summands). Similar procedures have, for example, been used in previous work with around-the-ear cEEGrid studies for sensor validation purposes (Debener et al., 2015; Knierim et al., 2021). To assess changes in cognitive load, the NASA Task Load Index (TLX) was completed after each task round. The TLX is a six-item multi-dimensional self-report instrument that collects perceptions of mental, temporal, and physical load, performance, effort, and frustration (Hart & Staveland, 1988). The TLX has been used in various experiments for similar purposes as ours (see, e.g., Grimes & Valacich, 2015). Figure 4 shows the study procedure with exemplary screenshots from the tasks. To assess the reliability of the main effects, each task was completed three times.

Figure 4. Study 1 procedure overview. First, a single participant (male, 33 years, wearing glasses – denoted A in Figure 5) completed this experiment four times (once per day) to gage the initial potential of the recording setup and to assess the reliability of detecting the main effects across sessions (within-subject group – WS). This is necessary, as previous EEG research has documented substantial within-subject variance of neural activations across recording sessions (Blankertz et al., 2016; Müller-Putz et al., 2015). Also, as a dry electrode system can be more prone to recording artefacts, it is important to study if an effect can be replicated for a single subject. Afterwards, four additional participants (1 female, age range = 24-31, median age = 28.5, none wearing glasses during the experiment – denoted B-E in Figure 5) completed a single session of the same experiment to also assess the between-subject reliability of the main effects (between subject group – BS). Participants were instructed to limit their movements during the experiment to reduce measurement artefacts.
The average duration of the experiment was 29.11 minutes. All subjects participated voluntarily, without remuneration, and were recruited from the academic staff of the authors’ institution. The recordings were conducted in an office building at the authors’ university to record data in a traditional office setting, that is, explicitly not a highly controlled laboratory. Upon arrival participants received an introduction to the experiment, the conditions of participation, including an explanation of the instrumentation and the following procedure. Before participation and sensor setup, all participants signed a consent form. Next, the headphone system was set up by the experimentator. That means signals were inspected for low and homogenous amplitudes (between 5 and 15 µV), and absence of PSD outliers which indicate poor electrode impedances on a particular channel. The data was recorded with OpenBCI GUI and the experiment was conducted through a browser interface (LimeSurvey), with local timestamp collection, thereby making sure that a single clock was used for the synchronization of the EEG data and the experiment markers.

8

Results

Following the recording, the data were processed as outlined above and the main effects investigated. First, the Berger effect was inspected by calculating the Alpha band power difference between eyes closed (EC) and eyes open (EO) resting phases at each electrode and repetition (block). Both the average PSD and the heatmap plot in Figure 5 show a clear and consistent Alpha power increase across sessions, blocks, and electrodes, when the eyes were closed, thereby confirming the ability of the headphone system to robustly detect this known and large neural effect. It should be noted that sporadic variation in the strength of the Alpha modulation from block to block occurred at individual electrode sites. This is an indication of some volatility of the signal collection performance of the dry electrodes that was here treated by averaging power distributions across electrode sites.

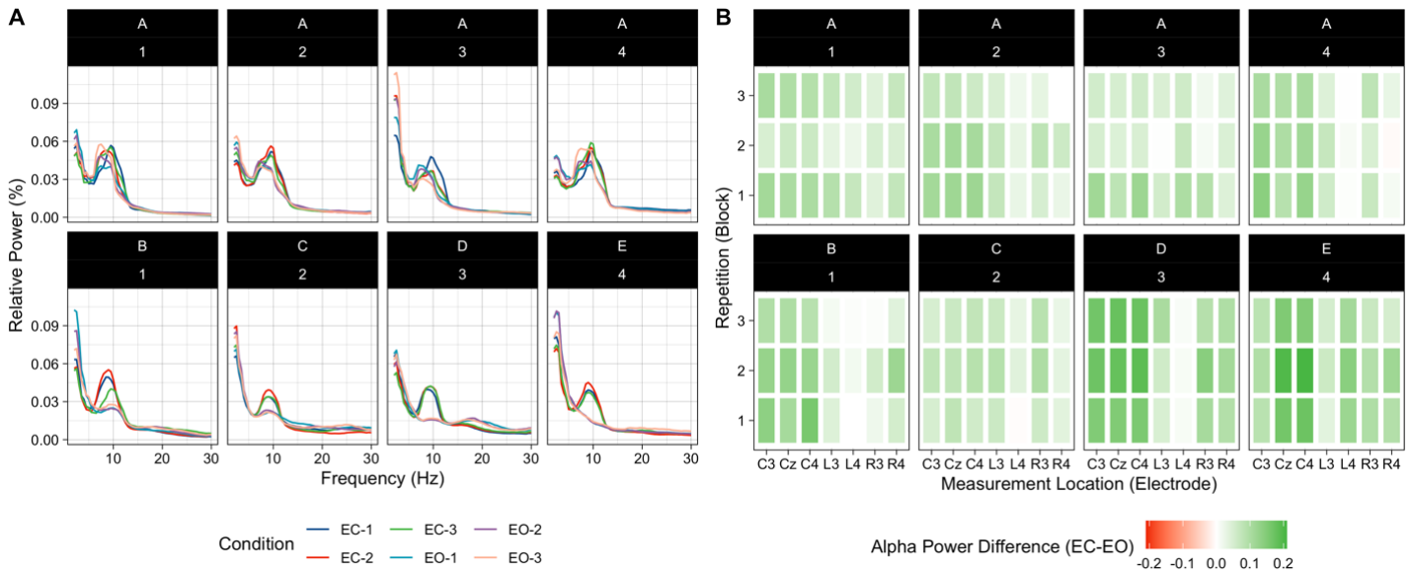
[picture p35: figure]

Figure 5. Berger effect replication – Alpha band power differences are shown for each participant. The top row shows the repeated single subject recordings. The bottom row shows four different participants. (A) shows the PSD in EC and EO phases, (B) the difference between EC-EO per electrode and block. Next, the cognitive load modulation was assessed. For this purpose, the TLX reports were aggregated in the recommended form (i.e., by summing the six items) for each measurement occurrence. A linear mixed model (LMM) with random intercept for each session was used to assess a main effect of task on perceived load (including the eyes open rest and both mental arithmetic tasks). An ANOVA based on this model confirms a clear main effect (p < .0001) with significant post-hoc contrasts that indicate a stepwise increase from rest to easier to harder mental arithmetic tasks (all p < .0001) – see Figure 6.

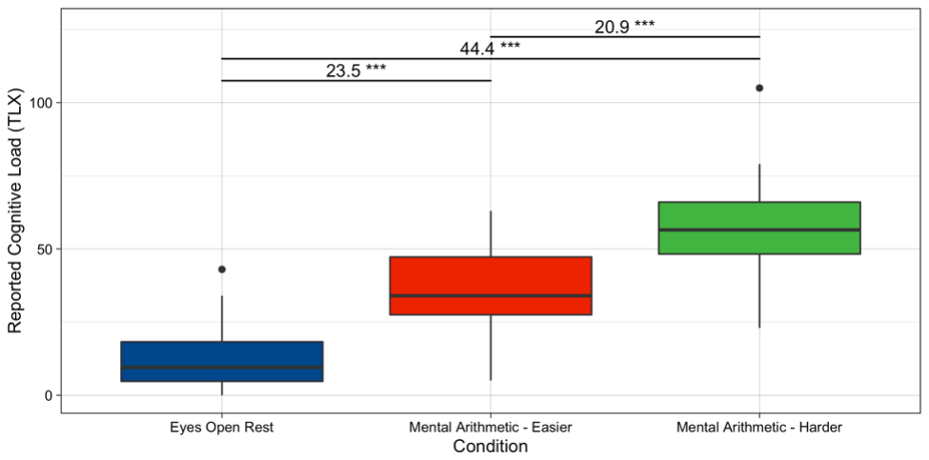
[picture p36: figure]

Figure 6. Load manipulation check study 1 – The perceived cognitive load increases from rest to easier to harder mental arithmetic. Values above boxes show median differences. Given this confirmed manipulation, we pursued a direct investigation of the perceived cognitive load with Theta and Alpha band power changes. Repeated-measures (RM) correlations were computed to account for

9

the substantial inter-individual difference in EEG recordings (Blankertz et al., 2016). Figure 7 shows the strong and significant positive (Theta) and negative (Alpha) correlations between frequency band powers and cognitive load reports. Notably, the correlations are robust for all the recording groups (the single-subject – WS, and the multi-subject – BS recordings), and for most electrode sites. This finding is expected and in line with related work (see, e.g., Wascher et al., 2019). However, the results also highlight that Theta relationships are more pronounced on the top of the head and that Alpha power relationships are weaker in channels L3 & L4. After additional signal inspection, we believe that the latter effect is most likely attributed to a noisy channel in two sessions. As the sample was very small, these channels were not removed. The aggregation to “Top” and “Ears” regions of interest (ROI) appears to manage this limitation.

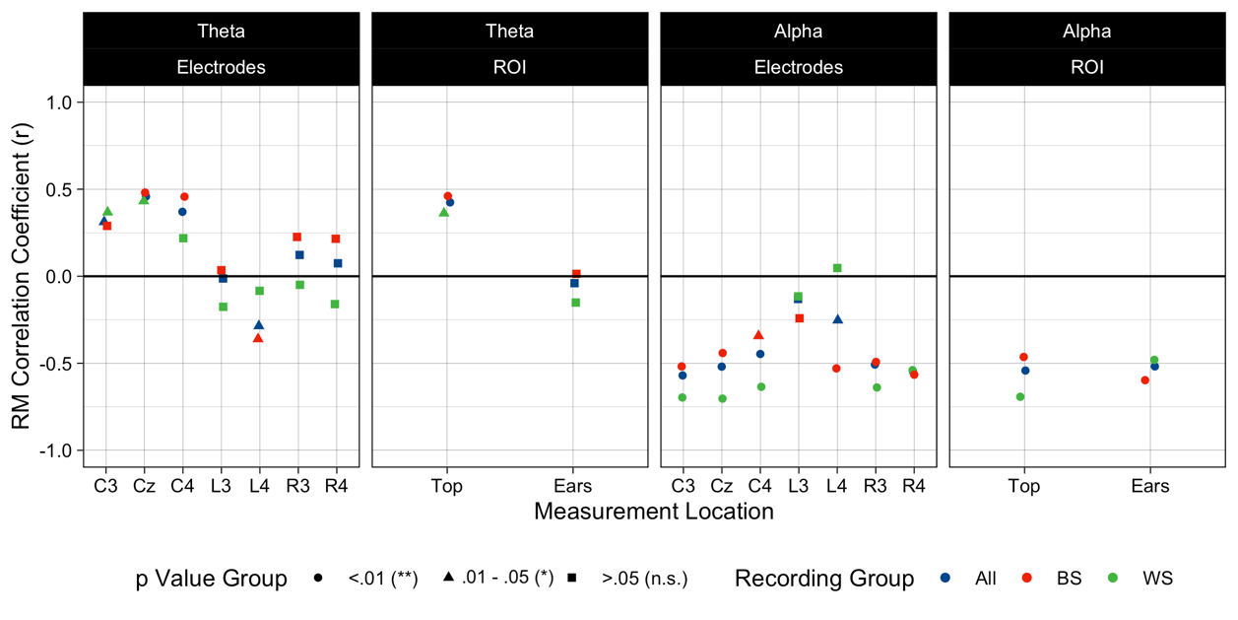
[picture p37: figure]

Figure 7. Correlations between EEG band powers and reported cognitive load. While these results provided good initial support for the main research question of detecting cognitive load changes due to such strong effects, it was still possible, that the findings are limited to the restricted experiment and small sample. Therefore, we pursued an extended second study with a larger sample, an additional difficulty variation, and two additional tasks to further assess the findings’ robustness.

### Study 2

Procedure

For the second study, we investigated three main effects: (1) the reliability of the load-frequency band relationships across more difficulty levels, participants, and tasks, (2) the influence of possible confounding variables on this relationship, and (3) we explored the relationship between cognitive load and flow experiences – a mental state with strong ties to productivity and well-being that is increasingly investigated in the IS discipline and the context of knowledge work (Knierim et al., 2019; Riedl et al., 2020). We explore this relationship based on a central premise of flow theory, that flow can emerge under situations of optimal challenge (Engeser & Rheinberg, 2008) – or, as we will elaborate on below, optimal cognitive load.
A set of tasks was chosen that represents primarily cognitive tasks, yet with a variation in mental, sensory, and motoric demands. Specifically, we implemented an experiment that manipulates task difficulty in mental arithmetic, puzzle, and text copying tasks, with three difficulty levels (easy, medium, and hard). The difficulties for each task and condition were calibrated in a pre-test of the experiment with six participants. In the (extended) mental arithmetic task, participants had up to 18 seconds to add a manipulated number of summands (2, 3, and 5 summands in the easy, medium, and hard task conditions respectively). The design was closely aligned with previous work (Knierim et al., 2019) and is otherwise identical to Study 1. In the puzzle task, participants had up to 30 seconds to assemble a picture puzzle with a manipulated number of pieces (2, 6, and 12 pieces in the easy, medium, and hard task conditions respectively). This task

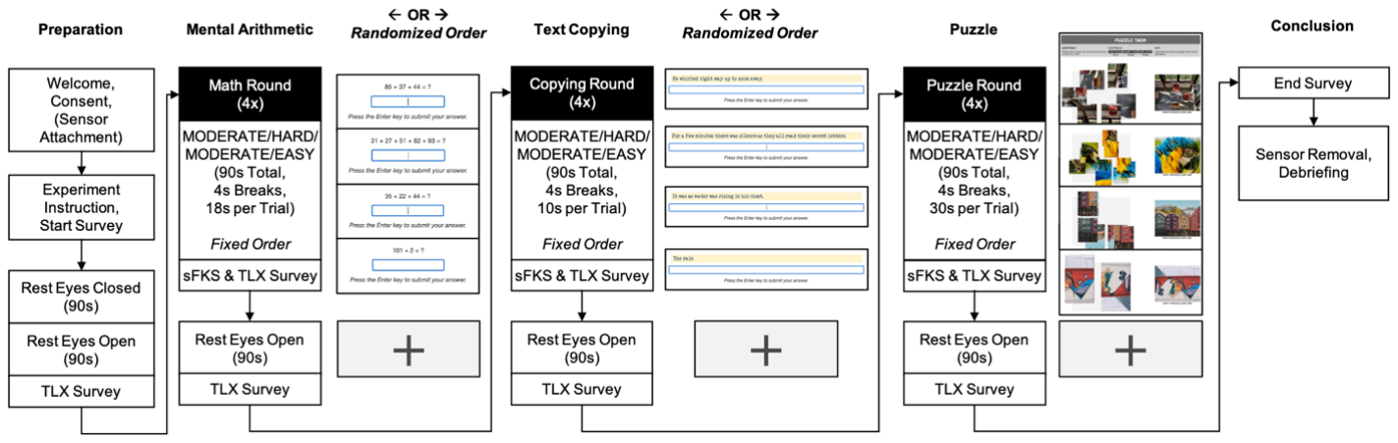
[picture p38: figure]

10

was added in contrast to the mental arithmetic task to provide a more visually stimulating task. Variations in visual stimulations have been documented as a possible challenge for cognitive load monitoring, especially as posterior Alpha band activity can be blocked by this factor (Blankertz et al., 2016). The task design was based on a related puzzle difficulty manipulation experiment (Tse et al., 2016).
In the text copying task, participants had up to 10 seconds to transcribe the text from a picture with a manipulated number of characters (9-10, 31-35, and 61-65 characters in the easy, medium, and hard task conditions respectively). This task was selected to provide additional variation in required motor action. Motoric activity (muscle movement) can represent a strong source of signal noise (Müller-Putz et al., 2015). Thereby, the robustness of the load-frequency relationships can be assessed further. The task design was closely related to a previous text copying difficulty manipulation experiment (Fest et al., 2021). Excerpts from a fiction novel were used as the content of the text snippets.
For all tasks, to ensure the differentiation of the easy and medium difficulty, the easy task condition showed only one of two pre-selected stimuli (e.g., only one of two puzzles – randomly drawn). Also, in all tasks, the task round lasted 90 seconds, with 4-second breaks between two consecutive stimuli. Examples of the difficulty in each task condition and the respective trial durations per task are shown in Figure 8. After an introductory task round in medium difficulty, participants completed a hard, then a medium, and lastly an easy difficulty task round. The order of the three tasks was randomized, with six possible orders. Each task round was followed by a short questionnaire including the NASA TLX to assess the perceived cognitive load, and three items from the flow short scale (FKS - Engeser & Rheinberg, 2008), with each item corresponding to the main flow dimensions in this scale (optimal challenge = “I felt just the right amount of challenge”, fluency = “My thoughts/activities ran fluidly and smoothly”, absorption = “I was totally absorbed in what I was doing”). We opted for this questionnaire design to limit the number of total questions, as the frequency of surveys was high. Lastly, each task type was preceded by an eyes-open resting stage.

Figure 8. Study 2 procedure overview. The data was again recorded with OpenBCI GUI and the experiment conducted through a browser-interface (oTree – Chen et al., 2016), again with local timestamp collection for precise synchronization of the EEG data and the experiment markers. The recruiting procedure and the experiment setup process were identical to study 1. The average duration of the experiment was 40.20 minutes. Overall 18 participants (6 female, age range = 21-34, median age = 27, 9 wearing glasses during the experiment) completed a single session of this experiment, thereby ensuring that each of the six possible task orders was completed three times. For one participant, only half of the experiment data was recorded due to a power outage in the experiment PC. Another participant was removed due to atypical EEG recordings, indicating that either the reference or ground electrode lost contact early during the experiment. Together with the absence of recording failures in study 1 the recording system thereby demonstrates good reliability.In this experiment, we also tracked the setup time from putting the headphones on to the start of the experiment to quantify some of the system’s usability aspects. The system was always set up by the same experimentator. The median setup duration (including signal quality inspection) was 4.14 minutes (min = 1.11 minutes, max = 13.91 minutes). Wilcoxon rank test results indicate a significant difference in setup time for gender (W = 60, p = .0245 – possibly caused by longer hair), and no significant difference in setup duration for participants wearing glasses (W = 49, p = .4894).

11

Results

Following the recording, the EEG data were processed as outlined in the methods section above. The self-reports were aggregated using the recommended methods (sum for the TLX and mean for the FKS). Before aggregating the FKS, we inspected the internal consistency of our shortened scale version, which was deemed acceptable with a Cronbach’s Alpha of .77.
As a manipulation check, we initially assessed the distribution of cognitive load (TLX) reports across the tasks. An LMM for each task with a random intercept for each session was used to assess main effects of difficulty conditions on perceived load. Ensuing ANOVA models confirm a clear main effect (p < .0001 for all three tasks) with significant post-hoc contrasts that indicate a stepwise increase from easier to medium, to harder difficulty conditions (all p < .0001) – see Figure 9. Notice, however, the clearer contrasts between easy and medium difficulties (when compared with the contrasts between medium and hard difficulties).

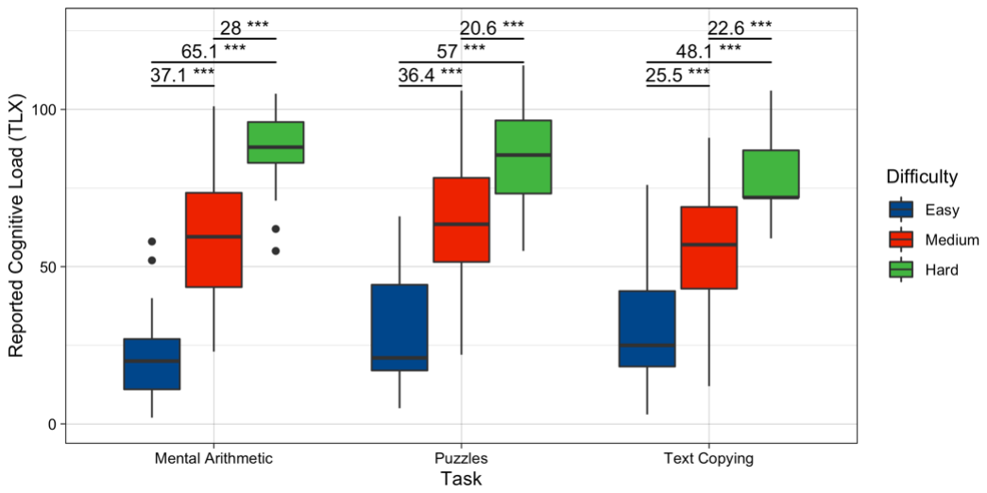
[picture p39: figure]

Figure 9. Load manipulation check study 2 –The perceived cognitive load increases from easier to harder task conditions. Values above boxes show median differences. Afterwards, the relationships between TLX reports and Theta and Alpha frequency bands were assessed. For this purpose, LMMs with frequency band power as a fixed effect and participant as random intercept were fitted for the two main ROIs: mean average band power on the top of the head (C3, Cz, C4), and around the ear (L3, L4, R3, R4). The models’ results are shown in Table 1. Significant positive relationships with Theta band power and highly significant negative relationships with Alpha band power are found in both regions. For the Theta band, the relationship with cognitive load is substantially weaker around the ears. The models also show a promising degree of explained variance, especially under consideration of both the random and the fixed effects.
Freq. Band | Theta | Alpha
ROI | Top | Ears | Top | Ears
Power Estimate (p Value) | 433.21 *** (p < .0001) | 98.53 * (p = .0199) | -299.04 *** (p < .0001) | -277.93 *** (p < .0001)
R² (Marg. / Cond.) | .35 / .64 | .03 / .06 | .16 / .19 | .15 / .19
Table 1: LMM results – EEG band power influence on reported cognitive load.
To further assess the possible influence of confounding variables – here: gender, glasses, and time, we included these variables as covariates in the aforementioned models. No significant relationships were found, which is why simple models were kept further throughout the remaining analyses. For a simplified relationship strength metric, please see additional RM correlation metrics in Figure 10. Here, it can also be seen that the relationship strength does not differ substantially for the three tasks.
Next, to assess the dependency of the relationship strength on experiment contrasts (i.e., to perform a sensitivity analysis), we systematically removed difficulty conditions from the data. For the first set (termed the “harder” set) we removed the easiest condition, for the second set (termed the “easier” set) the hardest condition, and for the third set all conditions except the two moderate difficulty rounds (termed the

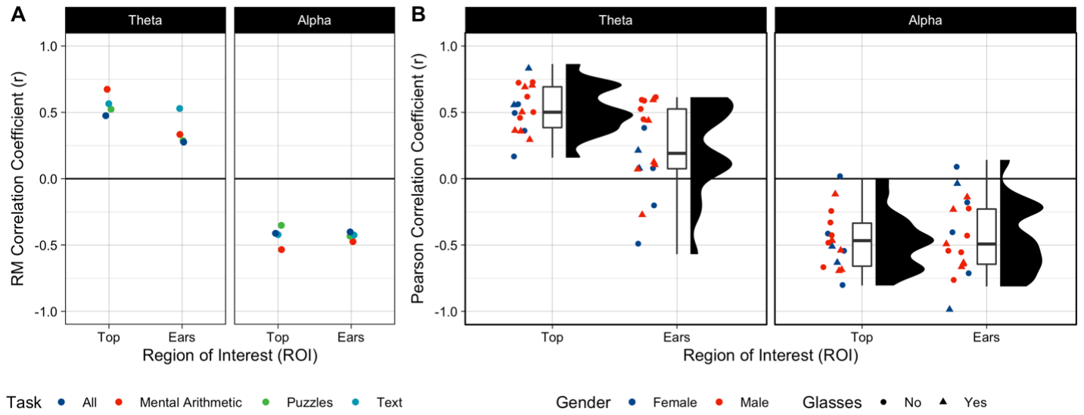
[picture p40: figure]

12

“medium” set). The results in Table 2 show that the load-power relationships become weaker, especially with the removal of the easier conditions, and especially so for the Theta frequency band. The effect remains significant and strong for the Alpha band, despite the contrast removal. This indicates a higher sensitivity for the Alpha band for load detection given the current experiment data and feature extraction process.
Freq. Band | Theta | Alpha
ROI | Top | Ears | Top | Ears
“Harder” Set (data without easiest conditions)
Power Estimate (p Value) | 98.45 * (p = .0281) | 40.896 (p = .3270) | -193.23 ** (p = .0028) | -186.80 ** (p = .0057)
R² (Marg. / Cond.) | .05 / .13 | .01 / .06 | .06 / .07 | .06 / .08
“Easier” Set (data without hardest conditions)
Power Estimate (p Value) | 236.71 *** (p = .0005) | 126.01 ** (p = .0075) | -270.87 *** (p < .0001) | -227.50 *** (p < .0001)
R² (Marg. / Cond.) | .22 / .40 | .07 / .12 | .17 / .24 | .14 / .19
“Medium” Set (data with only the medium difficulty conditions)
Power Estimate (p Value) | 26.84 (p = .5701) | 11.62 (p = .8210) | -209.30 ** (p = .0091) | -191.50 * (p = .0155)
R² (Marg. / Cond.) | .01 / .31 | .01 / .30 | .12 / .26 | .11 / .29
Table 2: Sensitivity analysis for EEG band power – reported cognitive load effects.
To further evaluate the relationship strength at a less aggregated level, Pearson correlations between TLX reports and frequency band powers were calculated for each individual participant. While the sample size for each individual is small, the average size of the correlation coefficients is in line with the previous analyses, showing strong load report relationships for Theta power on the top of the head and Alpha power in both ROI (see Figure 10). This plot also highlights that gender and glasses do not appear to systematically influence the strength of the load-power relationships. Interestingly, however, there is a substantial variance present for the load-frequency relationships at the individual level. On the one hand, this could be variance due to the small per-subject data points. On the other hand, it could indicate a potential for further improvement in the feature extraction approach.

Figure 10. Correlation coefficients for reported cognitive load – EEG band power relationships across tasks (A) and for individual participants (B).
Given the reliable load-band power relationships, we deemed it reasonable to further explore the potential of extending the investigation towards the connection between load, frequency bands, and flow experience. A central premise in the underlying flow theory is that the so-called “peak experience” can emerge under situations of optimal challenge when a balance of an individual’s abilities and the tasks’ demands occurs (Engeser & Rheinberg, 2008). In extension, we propose, that such a situation is more likely present, with moderate levels of cognitive load. In contrast, underload or overload are more likely related to the situations

13

in which a task is too easy or too hard for an individual. Some previous research has proposed a related pattern between flow and mental effort (Ewing et al., 2016). Also, it is repeatedly documented, that flow experience shows an inverted U-shaped relationship with a task’s difficulty (Engeser & Rheinberg, 2008; Knierim et al., 2019; Tozman et al., 2015). However, we are not aware of any research that has directly investigated the relationship between flow experience and subject (reported) and objective (frequency band) indicators of cognitive load. Therefore, to pursue this possibility for theoretical integration, we inspected the relationship between these variables. Using an LMM with load as a predictor for flow and a random intercept for participants, we initially found no significant, linear relationship. However, as previously mentioned, a non-linear relationship between the two variables is more likely to be expected. Adding a second order polynomial load term to the model shows a highly significant quadratic relationship (p <.0001 – see Figure 11). The substantial R² (marginal = .26, conditional =.42) further supports the strength of this relationship.

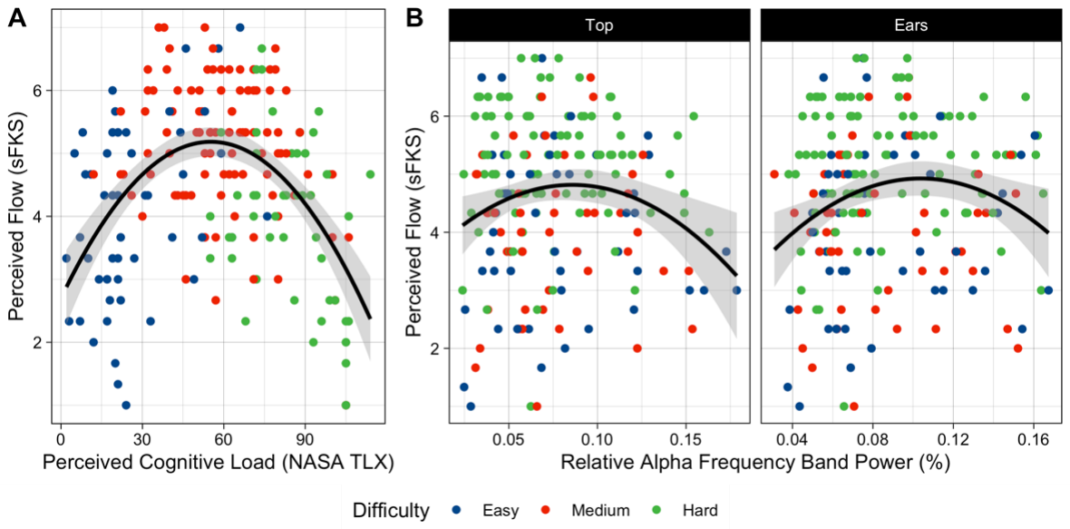
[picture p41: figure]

Figure 11. Inverted U-shape relationships between reported flow with reported cognitive load (A) and reported flow with Alpha band power (B). Given the strength of the self-report relationship, we also explored the connection between the EEG load indicators and flow with linear and quadratic mixed models (see Table 3). For Theta band power, no significant relationships are found. In contrast, for Alpha band power significant quadratic relationships are found on the top of the head and in the ear region. The interpretation and implications of these findings are discussed in the following section.
Freq. Band | Theta | Alpha
ROI | Top | Ears | Top | Ears
Linear Power Estimate (p Value) | -0.61 (p = .7952) | -2.01 (p = .4180) | -0.31 (p = .9370) | 2.81 (p = .4690)
Quadr. Power Estimate (p Value) | -2.11 (p = 0.2630) | -0.87 (p = .6321) | -3.70 * (p = .0202) | -3.61 * (p = .0255)
R² (Marg. / Cond.) | 0.01 / 0.17 | 0.01 / 0.15 | 0.04 / 0.17 | 0.04 / 0.15
Table 3: QMM results – EEG band power influence on flow.

### Discussion

The presented work aims to evaluate the applicability of 3D-printed dry-electrode EEG headphones for cognitive load monitoring. Thereby, we investigate if the principle of EEG-based load monitoring can be leveraged in a more convenient and ubiquitous form factor. The results from two controlled experiments show promising support for this purpose, yet also highlight remaining limitations and challenges.
First of all, it should be acknowledged, that the identified positive Theta and negative Alpha power relationships with variations of cognitive load are highly in line with previous EEG research (Berka et al.,

14

2007; Blankertz et al., 2016), as has been recently emphasized by a meta-analysis on this matter (Chikhi et al., 2022). Thereby, we assume a high internal validity of the presented findings, that is also supported by the reliability of the observations across studies, sessions, and tasks. We want to emphasize that these observations were achieved even without the use of dedicated measures to improve signal qualities that are typically used in EEG research. These measures often include hair washing, skin preparation, bad channel treatment, and stationary artefact removal (e.g., for eye blink artefacts or similar patterns – see Blankertz et al., 2016; Müller-Putz et al., 2015). Thereby, our findings not only confer with this established knowledge in the direction of the power-load effects but also with their location as Theta power load modulation is typically observed over frontal midline areas and Alpha power modulation at posterior brain regions (Chikhi et al., 2022). This observation highlights the utility of including electrodes on the top of the head for Theta change observation, which is, for example, not a feature that is available in around-the-ear cEEGrid electrodes. Therefore, the presented headset provides some advantages for load monitoring over other, wearable and transparent EEG systems.
Yet, while Chikhi et al. (2022) report Theta changes to be the most robust with load modulation, our findings stand in contrast as the Alpha power changes appeared clearly more reliable, and, importantly, more sensitive to changes in cognitive load. We consider two main explanations and approaches to overcome this limitation. On the one hand, it is possible that signal artefacts or bad channels contaminated the Theta band more strongly than the Alpha band that is typically pronounced in adults during wakefulness (Müller-Putz et al., 2015 – see also Figure 5). This explanation also appears possible, as related work reports on the extensive signal-cleaning efforts that were required to extract reliable frequency band load estimators due to the presence of movement artefacts (Wascher et al., 2019). On the other hand, it has been documented repeatedly, that especially the precise extraction of Theta band power, can be a challenging endeavor, as it is not represented similarly saliently as the Alpha band in the EEG signal PSD (Ewing et al., 2016; Naumann et al., 2016; Vallarino et al., 2021). It is therefore possible, that our present signal processing approach is insufficient in terms of artefact and/or bad channel removal, and/or Theta frequency extraction. The substantial variation in per-subject correlations of frequency band activity and perceived load would lend support to this proposition. More sophisticated signal processing methods like artefact subspace reconstruction (ASR) for signal reconstruction in artefact-laden data epochs (see, e.g., Wascher et al., 2019), and more sophisticated spectral filtering methods for Theta frequency extraction have already been reported (Naumann et al., 2016). The latter work even reports the potential of eliciting very high Theta power load sensitivity, up to the point of being able to predict the exact difficulty level in a Tetris game. Future work on the EEG headphone system should investigate the use of such approaches, not only for the sake of methodological improvements but for practical reasons. Reliance on Alpha power alone might be short-lived for load prediction in real-world environments as the power in the Alpha band can quickly become blocked in situations with strongly changing visual demands (Blankertz et al., 2016). Whether this is the case in knowledge work settings (especially such that include solitary work in front of a desktop PC), still needs to be investigated. The same needs to be said for other factors that could influence the systems capability for cognitive load monitoring, that have not yet been addressed systematically in this work. For example, while we do not find confounding influences of time on frequency band powers, such influences are known from neuroergonomics research, that investigates the detection of fatigue in system operators (for a discussion see Blankertz et al., 2016). Another factor is the question of how normal bodily movement during computerized work influences the usability of the Theta and Alpha bands for load detection. For these reasons, we propose to follow up our work with a study that bridges the controlled setting of the herein reported experiments with a controlled experience sampling study in the lab. In such a setting, study participants can complete controlled tasks (e.g., the mental arithmetic task in varied difficulty) and work on their own knowledge work project (e.g. a programming or scientific writing project) while being in a controlled environment. Data labels would then be generated by interrupting participants in a random interval (e.g., of 10, 15, or 20 minutes) during their typical work. Through multi-session participation, for example, for four one-hour sessions per day, a combination of internally valid and externally valid data can be recorded efficiently, while being able to monitor the correct administration of the sensing technology. Such a study design is proposed in Figure 12.

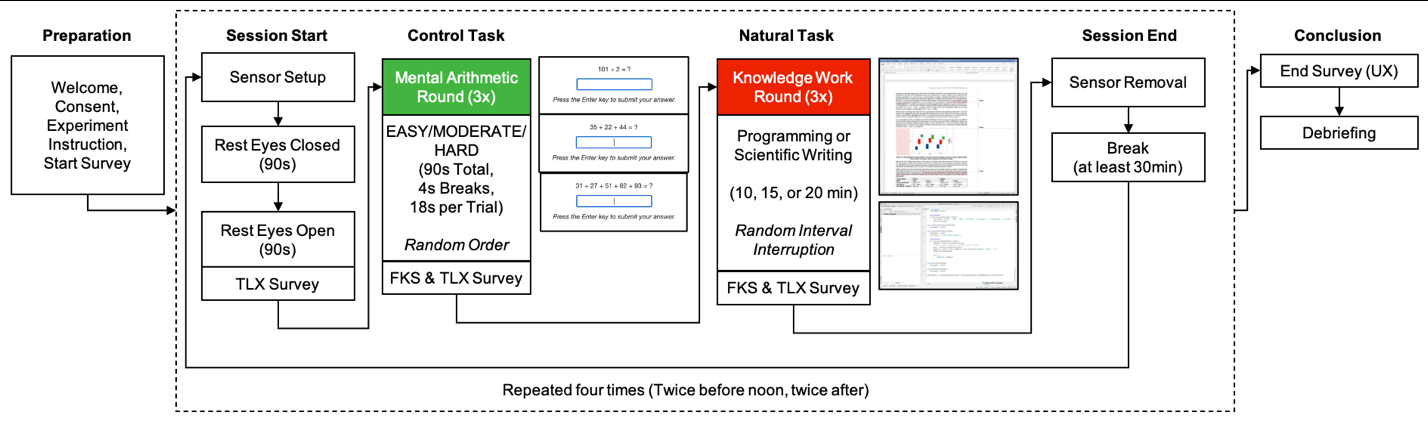
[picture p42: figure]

15

Figure 12. Follow-up study procedure overview. Finally, beyond the principle load detection potentiality, the last findings of our studies indicate an interesting application direction for the EEG headphone system. While cognitive load is often considered as relevant to productivity and health by the avoidance of high load (Galy et al., 2012; Lyu et al., 2015), it is rarely discussed, which positive outcomes might be realized from optimizing load levels. With the AI-driven growth of the knowledge work population (Frey & Osborne, 2017), it becomes an important goal for workers and organizations to manage not only overload and stress, but also foster positive psychological experiences. For this reason, we explored the relationship between cognitive load and flow experience, a mental state that is positively associated with peak performance, growth and subjective well-being (Engeser & Rheinberg, 2008; Knierim et al., 2019). Because flow experiences are said to be likely when a task is optimally challenging, it appeared reasonable to draw a parallel to situations of moderate cognitive load. Our findings on the inverted U-shaped load-flow report relationship and the supported quadratic fit for Alpha power and flow reports provide evidence that flow experiences could be observed and eventually fostered by monitoring load with our headphone EEG system. As the flow relationships with band powers were weak, it needs to be investigated further, how extensive this potential is. On the one hand, a quadratic Theta band relationship would have similarly been expected. As the Theta band showed less reliability for cognitive load changes too though, it is possible that too much heterogeneity masks the relationship. On the other hand, it is possible, that the flow-frequency relationship is biased on the report side from the shortened scale that we used to keep the questionnaire effort low during study 2. Future work should thus use a more comprehensive flow scale (e.g. the 10-item version by Engeser & Rheinberg, 2008) to avoid this limitation. Also, it is likely, that additional data variance is needed to realize the flow detection potential. Situations with a more intense flow experience should be observed to ascertain the existence of the observed relationship. Nevertheless, previous work has already hinted at the possibility of flow detection (Knierim et al., 2021), which is why the current results are considered promising.
As our dry-EEG headphone system might allow for more continuous and unobtrusive data collection, this theoretical and practical extension of cognitive load monitoring can be pursued well – if the reliability and usability of the system can be established further. Furthermore, as previous research has also shown relationships between heart rate variability changes and flow (Rissler et al., 2020; Tozman et al., 2015), and as previous cEEGrid work has shown that an ECG is retrievable from around-the-ear EEG recordings (Bleichner & Debener, 2017), the EEG headphone system might be the perfect candidate to elaborate on this application potential. As a matter of fact, this potential would also benefit the identification of cognitive load monitoring altogether, as EEG and ECG signal features are considered complementary and have even been recommended for this purpose (Chikhi et al., 2022).

### Conclusion

Through two controlled experiments, the present research demonstrates the promising potential of new, dry-electrode EEG headphones for monitoring cognitive load changes across multiple settings. Our research makes essential methodological, practical, and theoretical contributions to the IS discipline. In terms of methodology, we provide repeated and robust evidence that changes in cognitive load are well-observable in a system that is built on established measurement principles. Thereby, this EEG application leverages its sensing methods’ properties of unobtrusive, automatic, and real-time cognitive load observation. In practical terms, we provide a low-cost and easily reproducible hardware system with

16

material and assembly instructions. Thus, any interested IS researcher can put this sensing system to use and even develop similar ear-centered sensing systems (“earables” – see Röddiger et al., 2022). Lastly, in terms of theoretical knowledge, we empirically integrate the variable of cognitive load with flow experiences and highlight not only the conceptual but also the direct connection between neural correlates of cognitive load with perceived flow intensities.
Overall, while the system is not without limitations, we find the reliability and sensitivity of negative Alpha power changes with increased load, the clear observation of positive and substantial Theta power modulation, and the possibility of inferring flow experience intensities from these band powers exciting for the realm of knowledge work. This is because these observations are made possible by a cost-effective system that provides operational reliability and ease of use, as is demonstrated by the solid results despite the absence of extensive participant and data processing procedures. With the open-source and configurable nature of the system, scholars, enthusiasts, and practitioners are enabled to further pursue these research directions on their own for the sake of larger data set creations. Such broadened neurophysiological data sets will be essential as the foundation for mental state detection based on machine learning classifiers (Rissler et al., 2020). Therefore, such an openly available technology can hopefully serve as a catalyst for the development of positive adaptive technologies that not only prevent bad load situations like stress but can actively help to foster positive subjective experiences like flow. Importantly, this research is targeted at fruitful grounds in the IS domain, not only because the EEG headphones represent a sensing system in an accepted form factor, but also as the EEG is at the moment among the most frequent neurophysiological sensing method applied in the IS domain (Müller-Putz et al., 2015; Riedl et al., 2020).

### References

Athavipach, C., Pan-Ngum, S., & Israsena, P. (2019). A wearable in-ear EEG device for emotion monitoring. Sensors, 19(18), 1–16.
Babadi, B., & Brown, E. N. (2014). A review of multitaper spectral analysis. IEEE Transactions on Biomedical Engineering, 61(5), 1555–1564.
Barthélemy, Q., Mayaud, L., Ojeda, D., & Congedo, M. (2019). The Riemannian potato field: a tool for online signal quality index of EEG. IEEE Transactions on Neural Systems and Rehabilitation Engineering, 27(2), 244–255.
Berger, H. (1929). Über das Elektroenkephalogramm des Menschen. Archiv Für Psychiatrie Und Nervenkrankheiten, 87(1), 527–570.
Berka, C., Levendowski, D. J., Lumicao, M. N., Yau, A., Davis, G., Zivkovic, V. T., Tremoulet, P. D., & Craven,
P. L. (2007). EEG Correlates of Task Engagement and Mental Workload in Vigilance, Learning, and Memory Tasks. Aviation, Space, and Environmental Medicine, 78(5), 231–244.
Blankertz, B., Acqualagna, L., Dähne, S., Haufe, S., Schultze-Kraft, M., Sturm, I., Ušcumlic, M., Wenzel, M. A., Curio, G., & Müller, K.-R. (2016). The Berlin Brain-Computer Interface: Progress Beyond Communication and Control. Frontiers in Neuroscience, 10, 1–24.
Bleichner, M. G., & Debener, S. (2017). Concealed, unobtrusive ear-centered EEG acquisition: Ceegrids for transparent EEG. Frontiers in Human Neuroscience, 11(April), 1–14.
Brünken, R., Plass, J. L., & Leutner, D. (2003). Direct measurement of cognitive load in multimedia learning. Educational Psychologist, 38(1), 53–61.
Chen, D. L., Schonger, M., & Wickens, C. (2016). oTree-An open-source platform for laboratory, online, and field experiments. Journal of Behavioral and Experimental Finance, 9, 88–97.
Chikhi, S., Matton, N., & Blanchet, S. (2022). EEG power spectral measures of cognitive workload: A meta-analysis. Psychophysiology, 1–24.
Debener, S., Emkes, R., De Vos, M., & Bleichner, M. (2015). Unobtrusive ambulatory EEG using a smartphone and flexible printed electrodes around the ear. Scientific Reports, 5, 1–11.
Engeser, S., & Rheinberg, F. (2008). Flow, performance and moderators of challenge-skill balance. Motivation and Emotion, 32(3), 158–172.
Ewing, K. C., Fairclough, S. H., & Gilleade, K. (2016). Evaluation of an Adaptive Game that Uses EEG Measures Validated during the Design Process as Inputs to a Biocybernetic Loop. Frontiers in Human Neuroscience, 10, 1–13.
Fest, S., Kvaløy, O., Nieken, P., & Schöttner, A. (2021). How (not) to motivate online workers: Two controlled field experiments on leadership in the gig economy. The Leadership Quarterly, 32(6), 16. Frey, C. B., & Osborne, M. A. (2017). The future of employment: How susceptible are jobs to

17

computerisation? Technological Forecasting and Social Change, 114, 254–280.
Galy, E., Cariou, M., & Mélan, C. (2012). What is the relationship between mental workload factors and cognitive load types? International Journal of Psychophysiology, 83(3), 269–275.
Grimes, M. G., & Valacich, Joseph, S. (2015). Mind Over Mouse: The Effect of Cognitive Load on Mouse Movement Behavior. Proceedings of the 36th International Conference on Information Systems (ICIS), 1–13.
Hart, S. G., & Staveland, L. E. (1988). Development of NASA-TLX (Task Load Index): Results of empirical and theoretical research. Advances in Psychology, 52(1), 139–183.
Hu, P. J., Hu, H., & Fang, X. (2017). Examining the Mediating Roles of Cognitive Load With a Website : a Field Quasi -Experiment. MIS Quarterly: Management Information Systems, 41(3), 975–987. Kartali, A., Janković, M. M., Gligorijević, I., Mijović, P., Mijović, B., & Leva, M. C. (2019). Real-time mental workload estimation using EEG. International Symposium on Human Mental Workload: Models and Applications, 20–34.
Knierim, M. T., Berger, C., & Reali, P. (2021). Open-Source Concealed EEG Data Collection for Brain-Computer-Interfaces: Neural Observation Through OpenBCI Amplifiers with Around-the-Ear cEEGrid Electrodes. Brain-Computer Interfaces, 9(3), 161–179.
Knierim, M. T., Nadj, M., Li, M. X., & Weinhardt, C. (2019). Flow in knowledge work groups - Autonomy as a driver or digitally mediated communication as a limiting factor? Proceedings of the 40th International Conference on Information Systems (ICIS), 1–17.
Lyu, Y., Luo, X., Zhou, J., Yu, C., Miao, C., Wang, T., Shi, Y., & Kameyama, K. (2015). Measuring PPG-Based Stress-Induced Vascular Response Index to Assess Cognitive Load and Stress. Proceedings of the ACM CHI’15 Conference on Human Factors in Computing Systems, 857–866.
Martin, L., Hauret, L., & Fuhrer, C. (2022). Digitally transformed home office impacts on job satisfaction, job stress and job productivity. COVID-19 findings. PLoS ONE, 17(3), 1–23.
Müller-Putz, G. R., Riedl, R., & Wriessnegger, S. C. (2015). Electroencephalography (EEG) as a research tool in the information systems discipline: Foundations, measurement, and applications. Communications of the Association for Information Systems, 37(1), 911–948.
Naumann, L., Schultze-Kraft, M., Dähne, S., & Blankertz, B. (2016). Prediction of Difficulty Levels in Video Games from Ongoing EEG. International Workshop on Symbiotic Interaction, 125–136. Oostenveld, R., & Praamstra, P. (2001). The five percent electrode system for high-resolution EEG and ERP measurements. Clinical Neurophysiology, 112(4), 713–719.
Paas, F., Renkl, A., & Sweller, J. (2003). Cognitive load theory and instructional design: Recent developments. Educational Psychologist, 38(1), 1–4.
Rashid, U., Niazi, I. K., Signal, N., & Taylor, D. (2018). An EEG experimental study evaluating the performance of Texas instruments ADS1299. Sensors, 18(11), 1–18.
Riedl, R., Fischer, T., Léger, P.-M., & Davis, F. D. (2020). A decade of NeuroIS research: progress, challenges, and future directions. ACM SIGMIS Database: The DATABASE for Advances in Information Systems, 51(3), 13–54.
Riedl, R., Minas, R. K., Dennis, A. R., & Müller-Putz, G. R. (2020). Consumer-Grade EEG Instruments: Insights on the Measurement Quality Based on a Literature Review and Implications for NeuroIS Research. Lecture Notes in Information Systems and Organisation, 43, 350–361.
Rissler, R., Nadj, M., Li, M. X., Loewe, N., Knierim, M. T., & Maedche, A. (2020). To Be or Not to Be in Flow at Work: Physiological Classification of Flow using Machine Learning. IEEE Transactions on Affective Computing, Xxx, 1–12.
Röddiger, T., Clarke, C., Breitling, P., Schneegans, T., Zhao, H., Gellersen, H., & Beigl, M. (2022). Sensing with Earables: A Systematic Literature Review and Taxonomy of Phenomena. Proceedings of the ACM on Interactive, Mobile, Wearable and Ubiquitous Technologies, 6(3), 135–210.
Tozman, T., Magdas, E. S., MacDougall, H. G., & Vollmeyer, R. (2015). Understanding the psychophysiology of flow: A driving simulator experiment to investigate the relationship between flow and heart rate variability. Computers in Human Behavior, 52, 408–418.
Tse, D. C. K., Fung, H. H., Nakamura, J., & Csikszentmihalyi, M. (2016). Teamwork and flow proneness mitigate the negative effect of excess challenge on flow. Positive Psychology, 13(3), 284–289. Vallarino, E., Sommariva, S., Arnaldi, D., Famà, F., Piana, M., & Nobili, F. (2021). Transfreq: a Python package for computing the theta-to-alpha transition frequency from resting state EEG. In bioRxiv. Wascher, E., Arnau, S., Reiser, J. E., Rudinger, G., Karthaus, M., Rinkenauer, G., Dreger, F., & Getzmann,
S. (2019). Evaluating Mental Load During Realistic Driving Simulations by Means of Round the Ear Electrodes. Frontiers in Neuroscience, 13(September), 1–11.

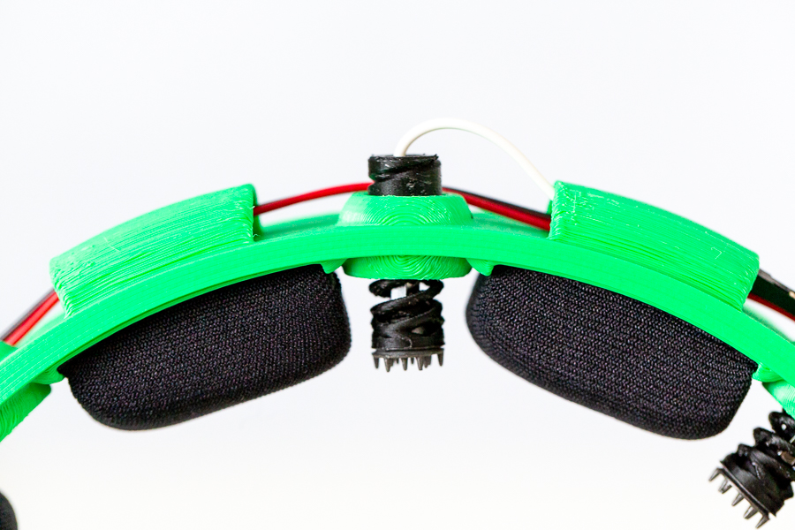
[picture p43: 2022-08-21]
imgs/_F5A7244.jpg

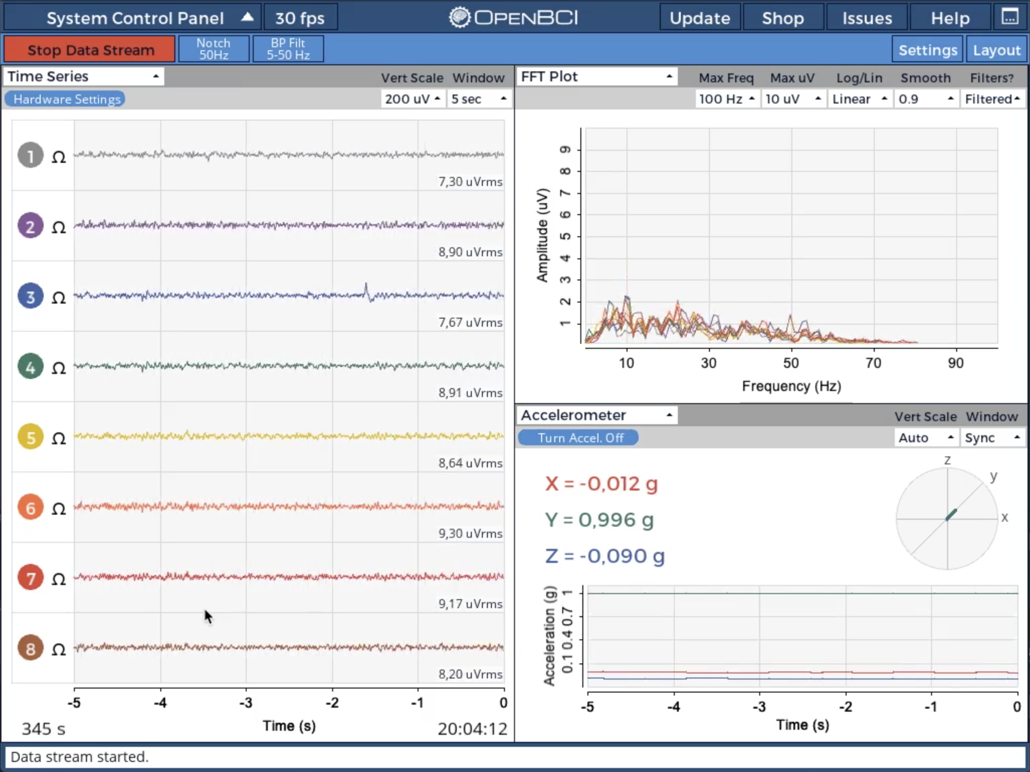
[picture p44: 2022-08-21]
imgs/clean_signals_example.png

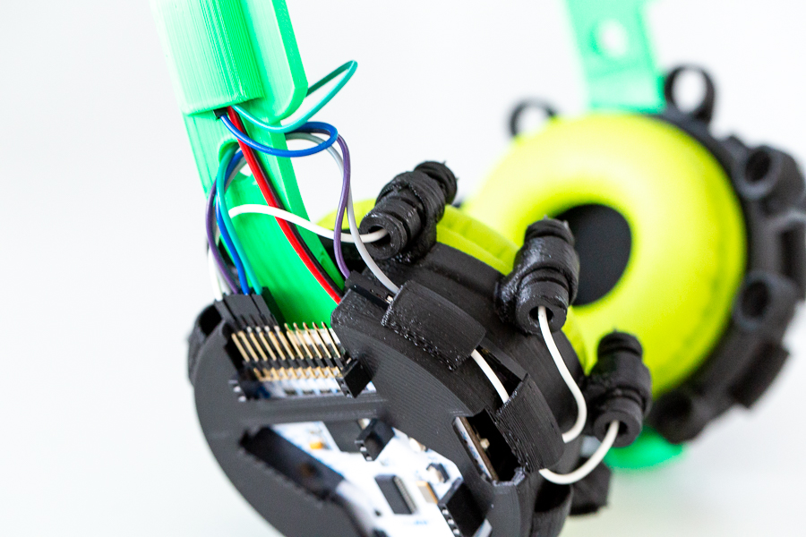
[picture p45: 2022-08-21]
imgs/_F5A7246.jpg

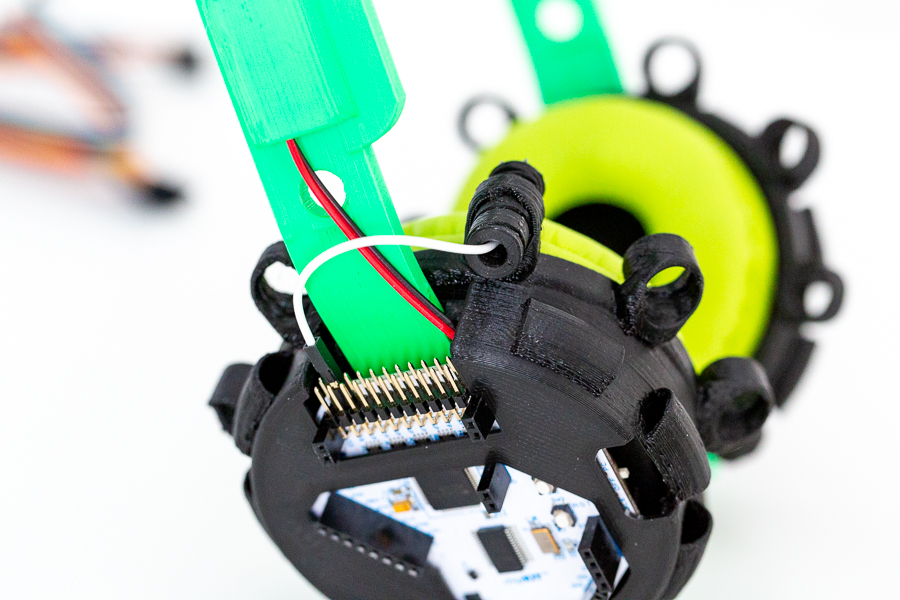
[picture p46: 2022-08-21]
imgs/_F5A7236.jpg

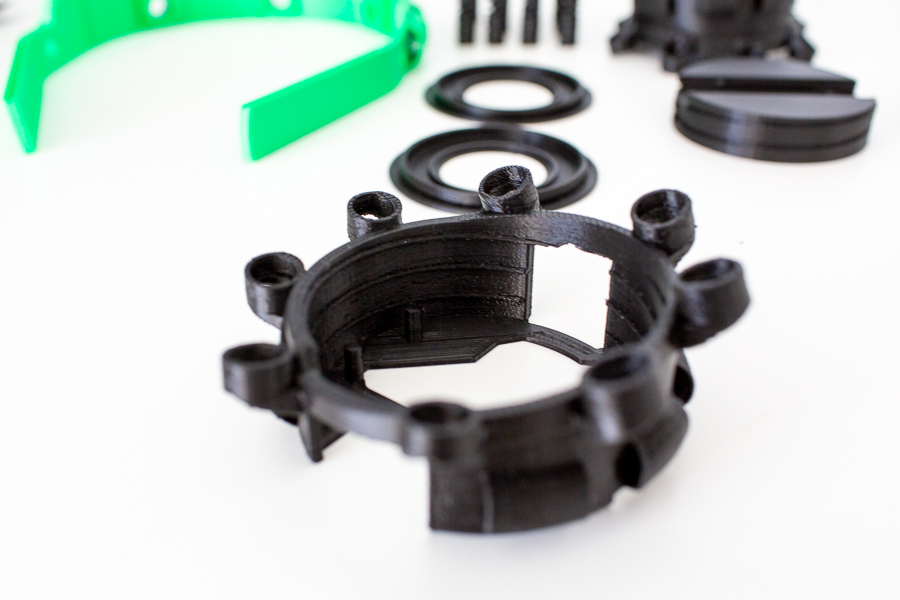
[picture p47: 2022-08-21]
imgs/_F5A7124.jpg

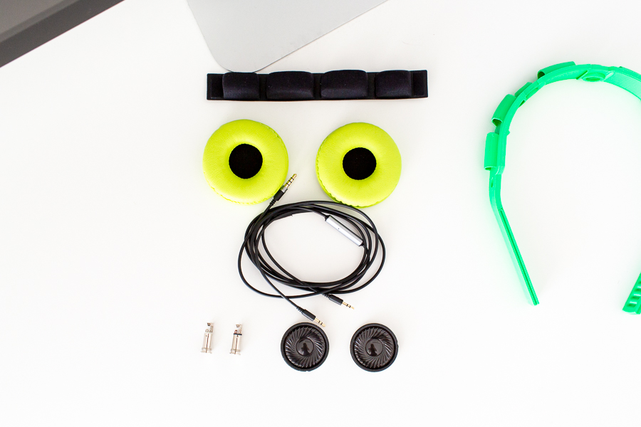
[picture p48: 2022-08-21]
imgs/_F5A7079.jpg

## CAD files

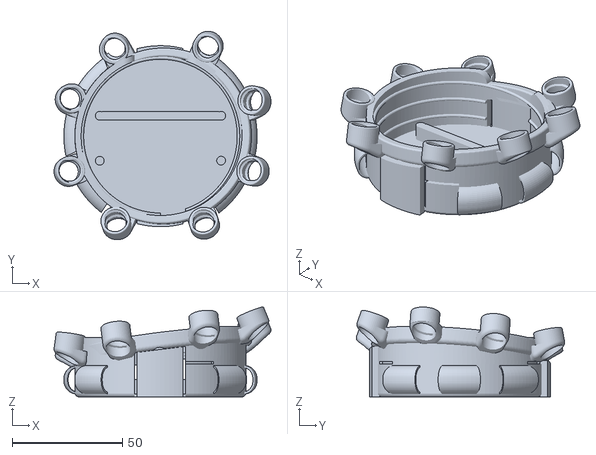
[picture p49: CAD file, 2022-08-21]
stl/EarOuterRight.stl
98.3 x 94.4 x 40.8

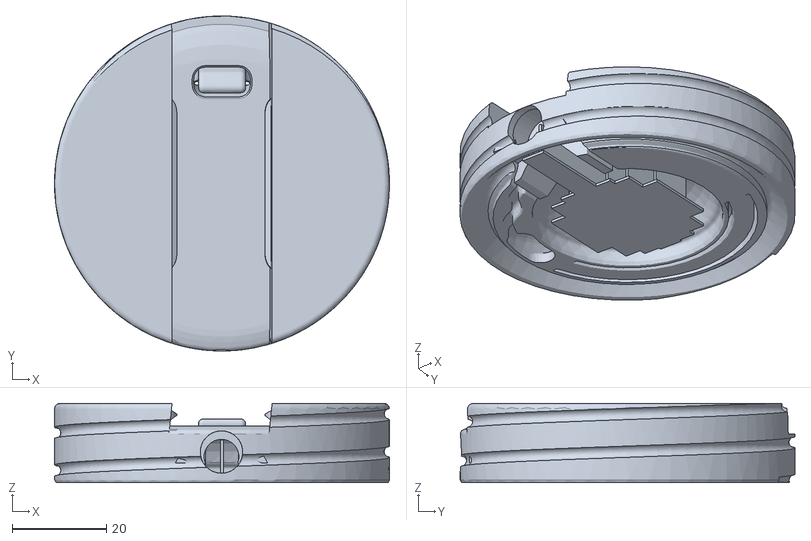
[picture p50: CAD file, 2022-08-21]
stl/EarInnerLeft.stl
71.0 x 71.0 x 16.8

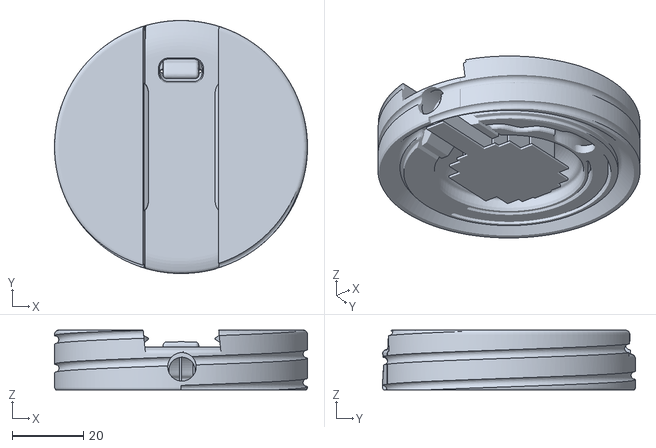
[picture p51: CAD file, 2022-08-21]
stl/EarInnerRight.stl
71.0 x 71.0 x 16.8

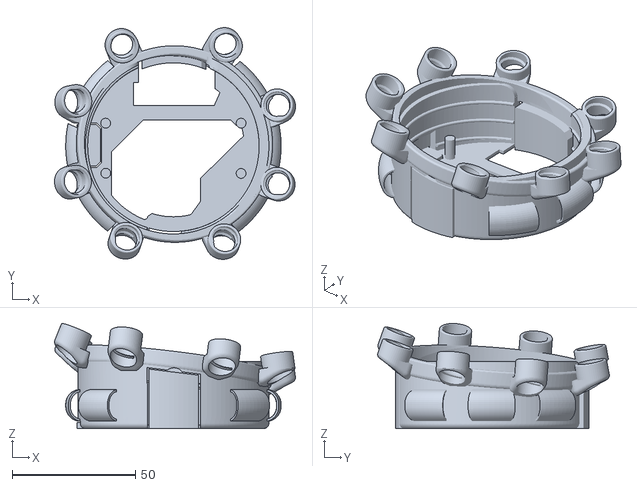
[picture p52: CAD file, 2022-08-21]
stl/EarOuterLeft.stl
97.9 x 94.1 x 42.7

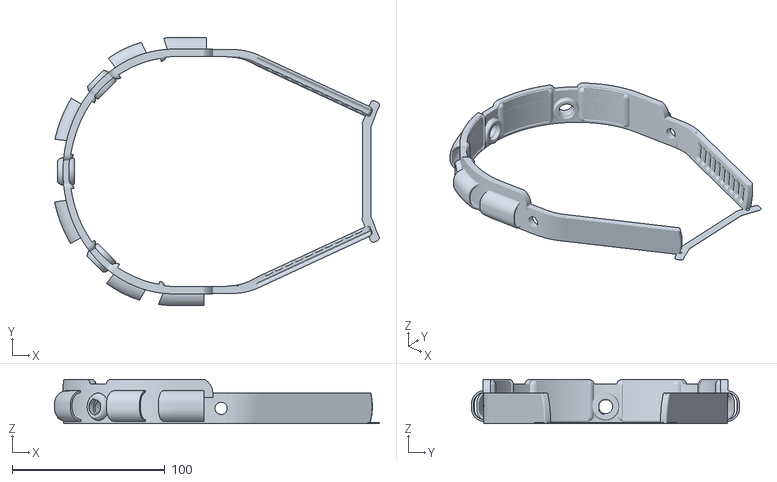
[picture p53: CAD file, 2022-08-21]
stl/Headband.stl
212.7 x 175.5 x 29.0
